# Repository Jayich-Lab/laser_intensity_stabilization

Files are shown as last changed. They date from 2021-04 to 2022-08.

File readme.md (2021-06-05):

# Laser Intensity Stabilization
<div align="center">
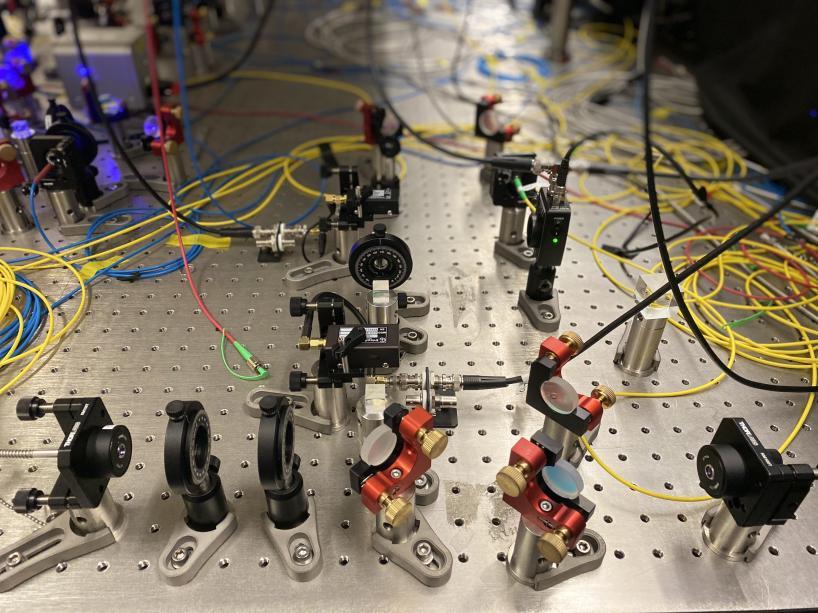
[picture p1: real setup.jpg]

</div>

[Development Notebook](https://docs.google.com/document/d/1RtXi4E6TiI_Ld4MZSRgFrHrQVlKGbRzDl3qZmrDYwTk/edit#)

We are aiming to stabilize intensity of laser to a fluctuation range of plus-minus 1% using Acousto-Optic Modulator (AOM) for a long timescale (in the order of days). This stabilization will improve the precision of experiments that use laser beams.

## Table of Contents
- [Motivation](#Motivation)
  - [P 3/2 Life Measurement](#P-32-Life-Measurement)
  - [Problems](#Problems)
  - [Goal](#Goal)
- [List of Components](#List-of-Components)
- [Schematics](#Schematics)
  - [Experiment Setup Schematics](#Experiment-Setup-Schematics)
  - [Acousto-Optics Modulator (AOM)](#Acousto-Optics-Modulator-AOM)
  - [Red Pitaya](#Red-Pitaya)
  - [Voltage Variable Attenuator (VVA)](#Voltag-Variable-Attenuator-VVA)
- [Feedback Loop](#Feedback-Loop)
  - [PID Controller](#PID-Controller)
  - [Code](#Code)
  - [Continuous (CW) Feedback](#Continuous-CW-Feedback)
  - [Pulsed Feedback](#Pulsed-Feedback)
- [Iterations](#Iterations)
  - [PI Stabilization](#PI-Stabilization)
  - [I Stabilization](#I-Stabilization)
- [Future Plans](#Future-Plans)
- [Contributors](#Contributors)

# Motivation
## P 3/2 Life Measurement
<div align="center">

</div>
We want to measure the lifetime of the P 3/2 lifetime of the radium-226 ion. For this measurement, we need to stabilize a detuned 802 nm laser which will be used for probing the  D 5/2 to P 3/2 transitions. The need for laser intensity stabilization comes from the concept of Rabi flopping. When we raise an ion from its ground state to an excited state, it doesn’t simply remain excited; rather, it oscillates back and forth from the ground state to the excited state at a frequency known as the Rabi frequency. The Rabi frequency is directly proportional to the laser intensity. If the laser intensity is not stable, then the excitation oscillation will shift. We will end up with ions between the excited and ground state, which will increase the systematic errors in our measurements. 

## Problems
Laser intensity drifts with time, and the amplitude drift could result in un-precise energy level transition, which affects energy shift induced by ac-stark shift of detuned laser. This unstable laser intensity affects the precision of Ra-226 excitation.

## Goal
Our goal for this research is to find a laser stabilization method that works for any lasers with any desired intensity. Users are able to manually set the desired intensity. The proportional and integral constants in the PID controller will be able to change on its own corresponding to the input signals.

# List of Components

- Photo Diode: [PDA10A2](https://www.thorlabs.com/thorproduct.cfm?partnumber=PDA10A2)
- Acousto Optic Modulator: [ATM-802DA1](https://intraaction.com/wp-content/themes/Divi/pdf/ATMModSeries08991.pdf)
- Laser: [SYNCROLASE-100](https://en.yuyiparts.com/aerotech-syncrolase-100-helium-neon-laser.html)
- Voltage Controlled Oscillator: [ZX95-100-S+](https://www.minicircuits.com/WebStore/dashboard.html?model=ZX95-100-S%2B)
- Voltage Variable Attenuator: [ZX73-2500-S+](https://www.minicircuits.com/WebStore/dashboard.html?model=ZX73-2500-S%2B)
- RF Amplifier: [ZHL-1-2W+](https://www.minicircuits.com/WebStore/dashboard.html?model=ZHL-1-2W%2B)

# Schematics
## Experiment Setup Schematics
<div align="center">
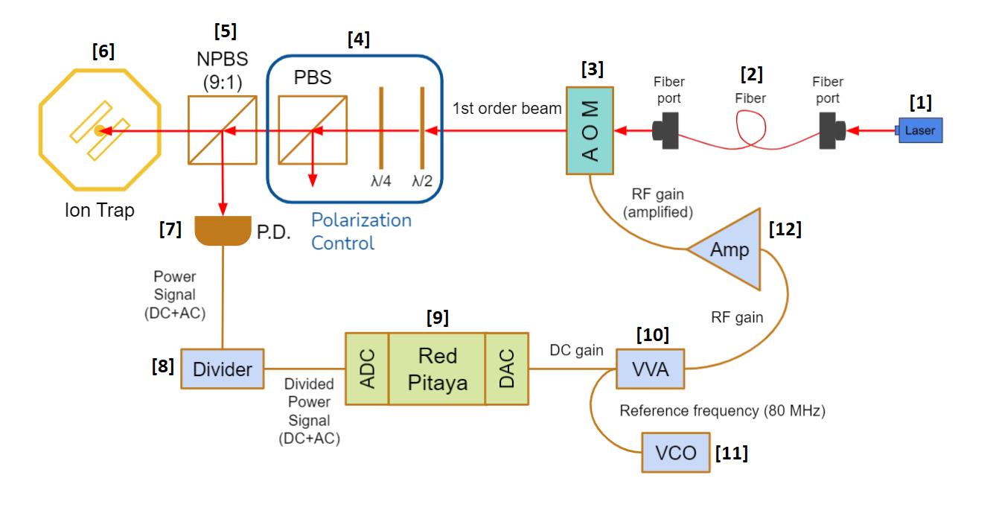
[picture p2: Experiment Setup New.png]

</div>

First, the laser beam [1] is transmitted by the fiber and goes through the two fiber ports [2]. It then is received by the [Acousto-Optic Modulator (AOM)](#Acousto-Optics-Modulator-AOM) [3], which diffracts the light to different intensity. We use the first order beam in our project. Next, the beam coming out from the AOM goes through the PBS (Polarizing Beam Splitter) [4] and the NPBS (Non-Polarizing Beam Splitter) [5]. These two beam splitters split the light and control the amount of light that goes into the ion trap [6] and the photodiode [7]. We choose an NPBS that splits 90 percent of the light and lets 10 percent of the power go into the photodiode. The photodiode is the detector of laser intensity in our project. It converts the light signal into voltage, which can then be received and analyzed by the PID program in Red Pitaya. The photodiode generates a voltage signal in the range of ± 4 volts and outputs it to the Red Pitaya. A ¼ divider [8] is put between the photodiode and the Red Pitaya to compensate the limitation that Red Pitaya can only take a voltage from -1 to 1 volt. A PID program is built in [Red Pitaya](#Red-Pitaya) [9]. It collects signals from the photodiode and compares it to a setpoint voltage to create an error signal. The Red Pitaya will then return this DC gain error signal and send it to a [voltage variable attenuator (VVA)](#Voltage-Variable-Attenuator-VVA) [10]. VVA receives this DC gain signal as well as an RF reference signal sent from the VCO (voltage control oscillator) [11], and it will output an attenuated RF gain with attenuation determined by the input control voltage (see the attenuation graph in the VVA section). The RF gain is then amplified by an RF amplifier [12] and sent back into the AOM to alter the intensity that goes through it.

## Acousto-Optics Modulator (AOM)
<div align="center">
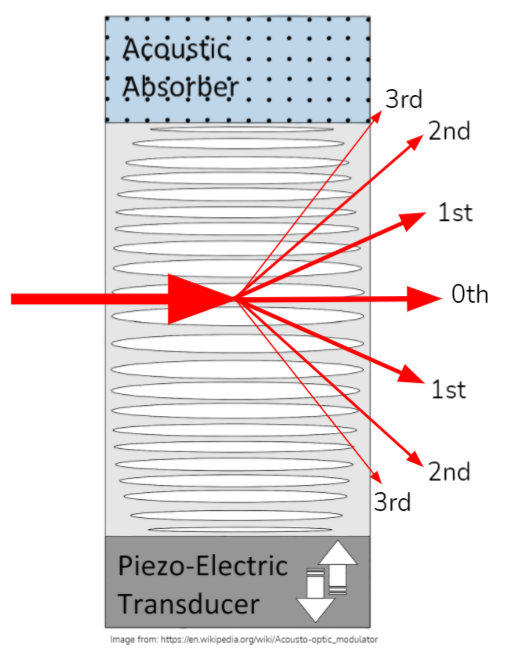
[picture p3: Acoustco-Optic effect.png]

</div>

An AOM uses the acousto-optic effect, which is similar to the Bragg diffraction, to diffract and shift the frequency of the incident light. The acousto-optic effect describes the diffraction of light by acoustic waves. The basis of this effect is a general effect of photoelasticity consisting in the change of the medium permittivity under the action of a mechanical strain. With the acousto-optic effect, the amount of light diffracted by the sound wave depends on the intensity of the sound. Thus, we use the intensity of the sound to modulate the intensity of the light.

For our project, we choose the first order beam from the AOM. The difference between each order beam is that they have different dynamic ranges. The dynamic range is the ratio between the largest and smallest values of the intensity that can be outputted by the AOM. For the zeroth order beam, the intensity can be attenuated from 100 percent to 20 percent, which provides a dynamic range from 100 to 300; while for the first order beam, the intensity can be attenuated from 85 percent to 0 percent, which provides a dynamic range from 100 all the way to infinity. Thus, we choose the first order beam for our project to have a larger dynamic range.

The intensity of the first order beam is controlled by the control signal that goes into the AOM. When the control signal increases, the intensity increases correspondingly. We adjust the intensity of the laser using this property of the AOM.

## Red Pitaya
<div align="center">
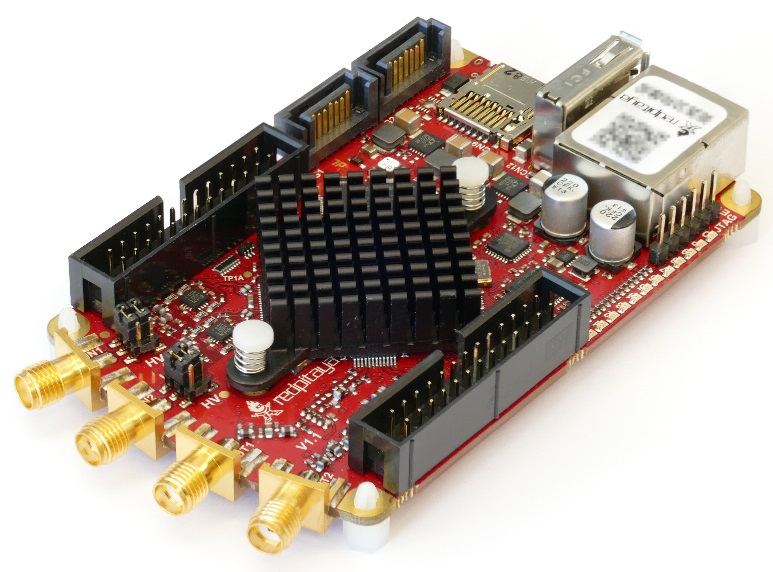
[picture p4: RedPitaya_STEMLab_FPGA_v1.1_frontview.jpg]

</div>

Red Pitaya is an affordable, PC based, multi instrument. It acts as the brain of our project, which takes up the role of PID controller for the feedback loop (Discussed in Feedback Loop Section). Signal coming from the photodiode is received by the DAC portal of the Red Pitaya, and after the PID program an output signal will be sent out from the ADC portal to the voltage variable attenuator (VVA).

## Voltage Variable Attenuator (VVA)
<div align="center">
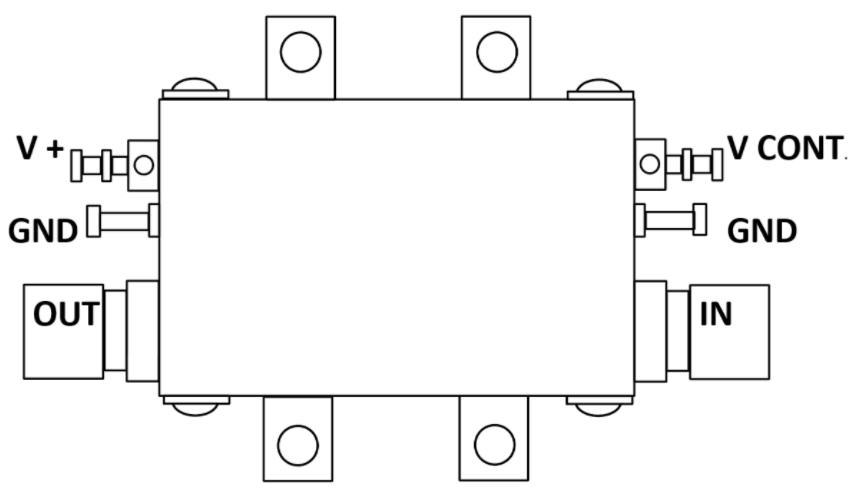
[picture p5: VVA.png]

</div>

Attenuators are transmission line components used to reduce the input power in a system by a predetermined amount. It is operated throughout its entire dynamic range. Different from fixed attenuators, variable attenuators can be controlled to vary the attenuation level of the device with a number of different methods. A voltage variable attenuator, the VVA, has its attenuation controlled by the voltage. The typical attenuation of the VVA we use, ZX73-2500+ attenuator, is shown in the figure below.
<br>
<div align="center">

</div>

From the figure above, we can see that the attenuation of our ZX73-2500+ attenuator is non-linear, with the curve relatively linear and flat at control voltage range 0 to 0.5 volts and at high voltage. These linear regions imply that at these two control voltage ranges, the attenuation of the VVA does not change dramatically under large control voltage change. This property of the VVA helps to diminish the overcompensation of the PID program and prevent it from destroying the whole feedback loop. An overcompensation of the PID program means that the PID overcompensates for every positive error and creates an even larger error in the negative direction (and vice-versa). With a VVA in the circuit, the overcompensation from the PID feedback can be diminished and it will not cause serious failure in the stabilization. To achieve high precision, we require the input control signal at higher voltage. We choose 4-12 volts as our range of control voltage in our project.

# Feedback Loop
## PID Controller
<div align="center">

</div>

Red Pitaya is remotely controlled using a client on a computer via an internal network. After receiving the signal, the pitaya runs a python script (discussed in [Code](#Code)) section, compares the input voltage to the setpoint voltage, and applies a control signal, C, which depends on the proportional, integral and differential terms of the error signal. The relationship can be seen in the equation above. We neglected the differential term for our setup as we weren’t concerned with stabilizing at high frequency (laser fluctuations tended to be low frequency). The control signal from the pitaya goes through an operational amplifier which increases the control range from ± 1 volt to 4 and 12 volts. The [Voltage Variable Attenuator (VVA)](#Voltage-Variable-Attenuator-VVA) section explains why we want to be in the 4 -12 voltage range. The control signal was also sent to an oscilloscope at the same time. The majority of the data was taken on an oscilloscope. The data from the oscilloscope was read by a server on the computer and sent to the red pitaya. The computer (server and client) are constantly communicating with the red pitaya during  the feedback loop. 

## Code
The programming was mainly done on the red pitaya using python and the PyRPL module, which has python defined classes for controlling the pitaya outputs and inputs. The PyRPL code was written onto a server, and a client was then made using that server. 
There was also a simpler script made for an independent laser intensity stabilization setup using an Arduino due. The code is above under “PI_Stabilization.ino”. The Arduino presents versatility as it uses C++, a widely accessible programming language. On the other hand, the red pitaya can either be programmed using the limited PYRPL module or the native language of the pitaya, Verilog, which is less accessible. 
Either the Arduino or the pitaya is sufficient for stabilization. Still, when it comes to pulsed feedback (discussed shortly), the Arduino is a better choice as C++ is easier to work with than Verilog. 

## Continuous (CW) Feedback
<div align="center">
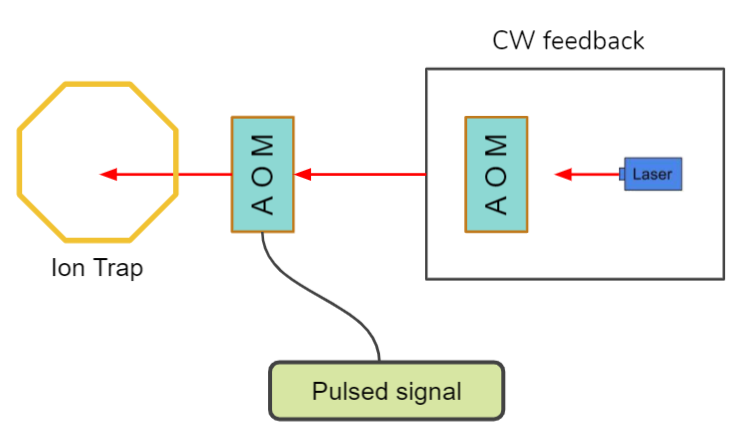
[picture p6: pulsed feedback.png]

</div>

We need to identify a clear distinction between continuous and pulsed feedback. In this experiment, we are applying continuous waveform (CW) feedback. We are continuously reading data and stabilizing it over time. The picture above illustrates a summary of our CW feedback in a rectangle on the right. Generally, in ion trap experiments, laser beams are sent to the ion trap in pulse sequences (on the order of microseconds). We can create a stabilized pulsing laser by placing a second AOM after the laser is stabilized. The second AOM will receive a signal that turns it “on” or “off,” This way, we have a pseudo pulsed feedback setup. 

## Pulsed Feedback
<div align="center">

</div>
We created pseudo pulsed feedback, but what does pulsed feedback look like? Unlike CW feedback, in pulsed feedback, we only take data on short intervals (µs). The above graph models a pulse sequence where the laser is on for µs and off for ms. During the period the laser is on, a microcontroller collects data and generates an error signal E1. When the laser is off, the microcontroller outputs a constant dc offset. After the laser is turned on again, a fixed dc voltage (red line) is outputted based on the error signal E1. This process continues for all pulses.
<br>
*Note only CW feedback was used in this project 

# Iterations
## PI Stabilization
<div align="center">

</div>
<br>

Laser intensity was stabilized to ± 0.2%, which surpasses our goal of ± 1%. The blue plot is the signal received by the photodiode, the orange curve is the control signal output by the red pitaya, and the green line is the stabilized signal.  We took the data in 8 hours and found no drifts in the stabilization, which indicates that our setup is robust since it maintains the same intensity while environmental parameters such as temperature change. Using only the P and I terms, we were able to minimize the initial noise by a factor of 200. 
<br><br>

<div align="center">
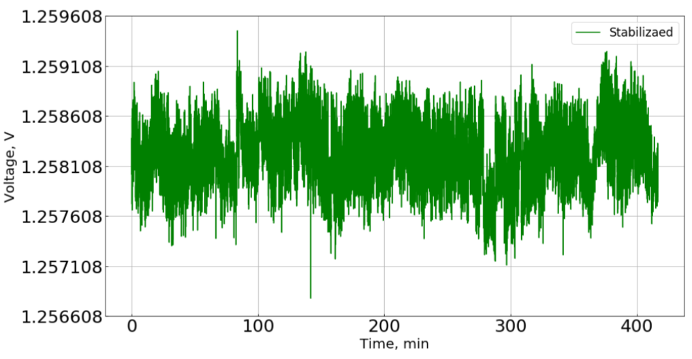
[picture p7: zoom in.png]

</div>
<br>

Looking more closely at the stabilized signal, we can see no long-term drift; the signal only oscillates at high frequency. This high-frequency noise can be accounted for by the internal noise of the photodiode. The ± 0.2% fluctuation in our data was partly correlated to the photodiode uncertainty; the rest of the noise comes from the control signal output by the pitaya. The above data set was preliminary data and demonstrated the sufficiency of our stabilization for the P 3/2 life measurement. 

## I Stabilization
<div align="center">
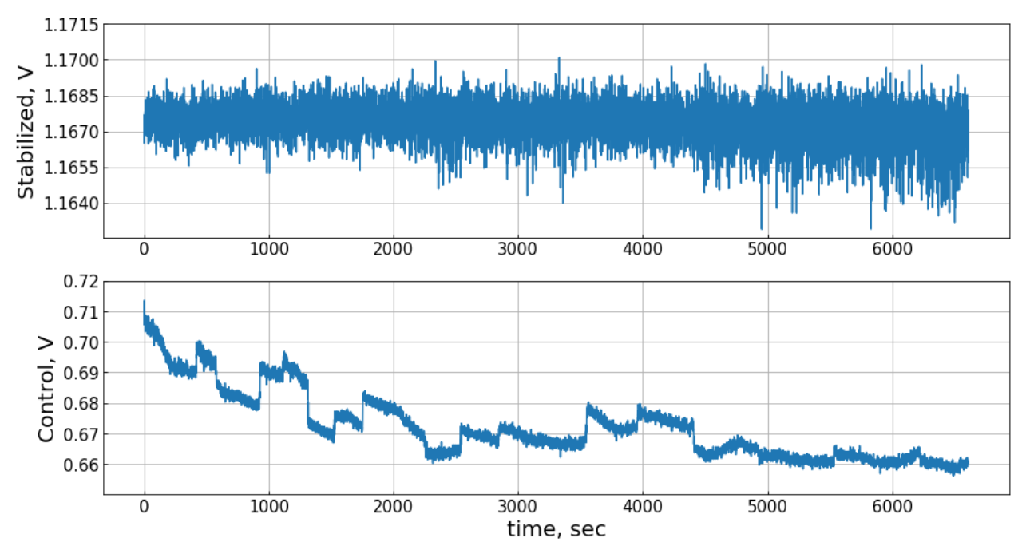
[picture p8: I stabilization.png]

</div>

Using 802 nm laser light (20% intensity fluctuation without stablilization), we stablilized the laser to average within ± 0.1% of our setpoint intensity. Extreme peaks during stablization still stayed within ± 0.3% of setpoint.  Long term drift of intensity from 802 nm is no longer a problem with this intensity stabilizer. The graph above was taken  on the laser that was used for the P 3/2 life time measurement. 

Observations:
1. It was found that **omitting** the proportional term for PID control was more stable than including proportional control.
2. The lower the control voltage (shown in the bottom graph as it slopes downward), the less stablity we get due to the VVA response curve at different voltages.

# Future Plans
<div align="center">
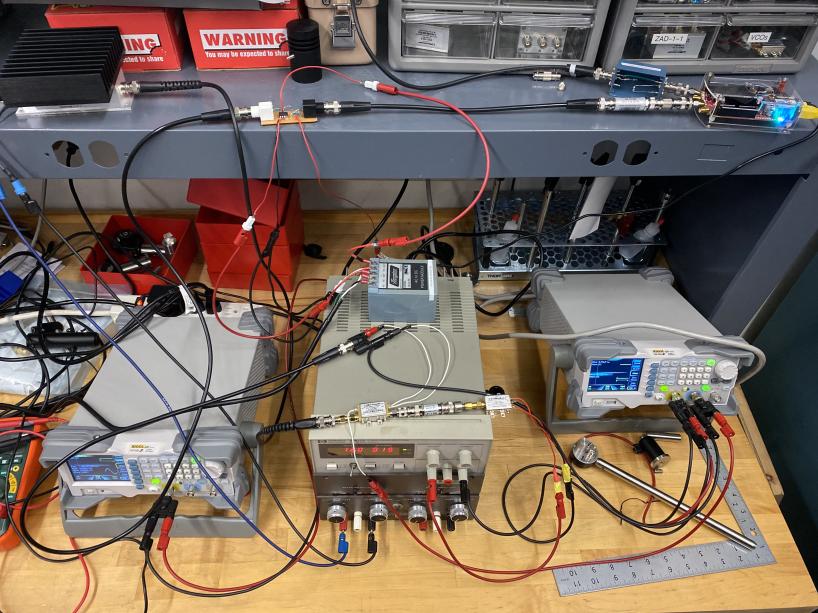
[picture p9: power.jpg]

</div>
<br>

There are some issues with our current pseudo pulsed feedback setup. 1) We can’t stabilize the laser intensity right before the beam reaches the ion trap; it has to go through different optics before reaching the trap, which means it will incur some extra noise that we can’t currently stabilize. 2) The second AOM (the one receiving pulsed signal) changes how fast it can turn on and off based on the environmental temperature. 3) Our current setup, as you can see from the picture above, uses too many separate power supplies, which makes it difficult to set up and apply to any measurement. 
Potential solution: utilize an [Arduino DUE](https://store.arduino.cc/usa/due) to make independent pulsed feedback. This would eliminate the second AOM and allow us to stabilize the laser light right before it reaches the ion trap.We would also be able to make an integrated power supply, making our stabilization more compact and robust. 

# Contributors
This project is made for CS 15C class by Chaoshen Zhang, Sam Gebretsadkan, Vivian Liao and Rei Landsberger.

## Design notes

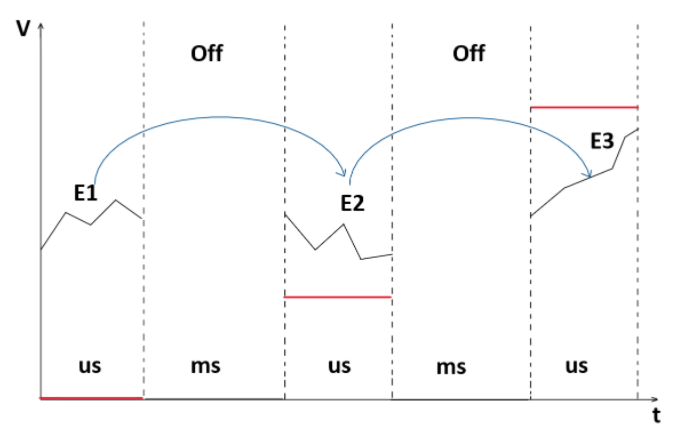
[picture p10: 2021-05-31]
pulsed feedback fig.png

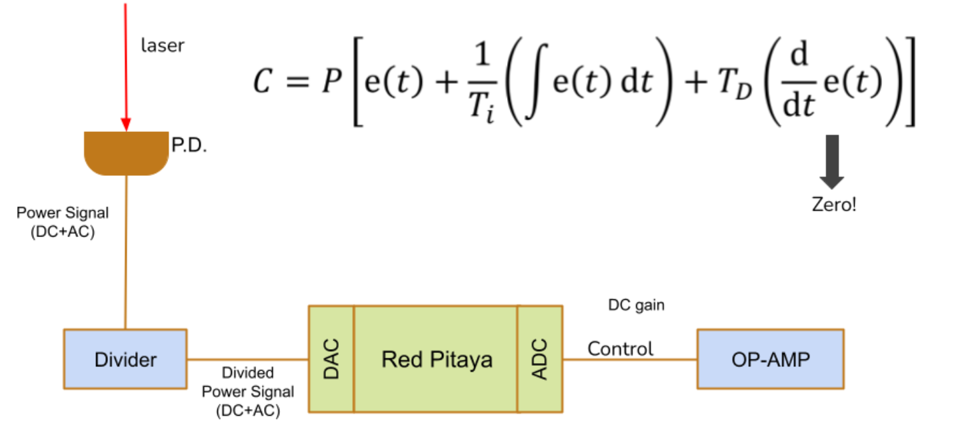
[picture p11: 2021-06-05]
PID controller.png

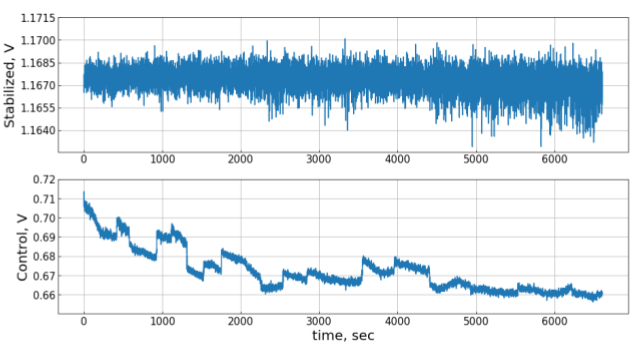
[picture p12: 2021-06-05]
802nm_stabilization.png

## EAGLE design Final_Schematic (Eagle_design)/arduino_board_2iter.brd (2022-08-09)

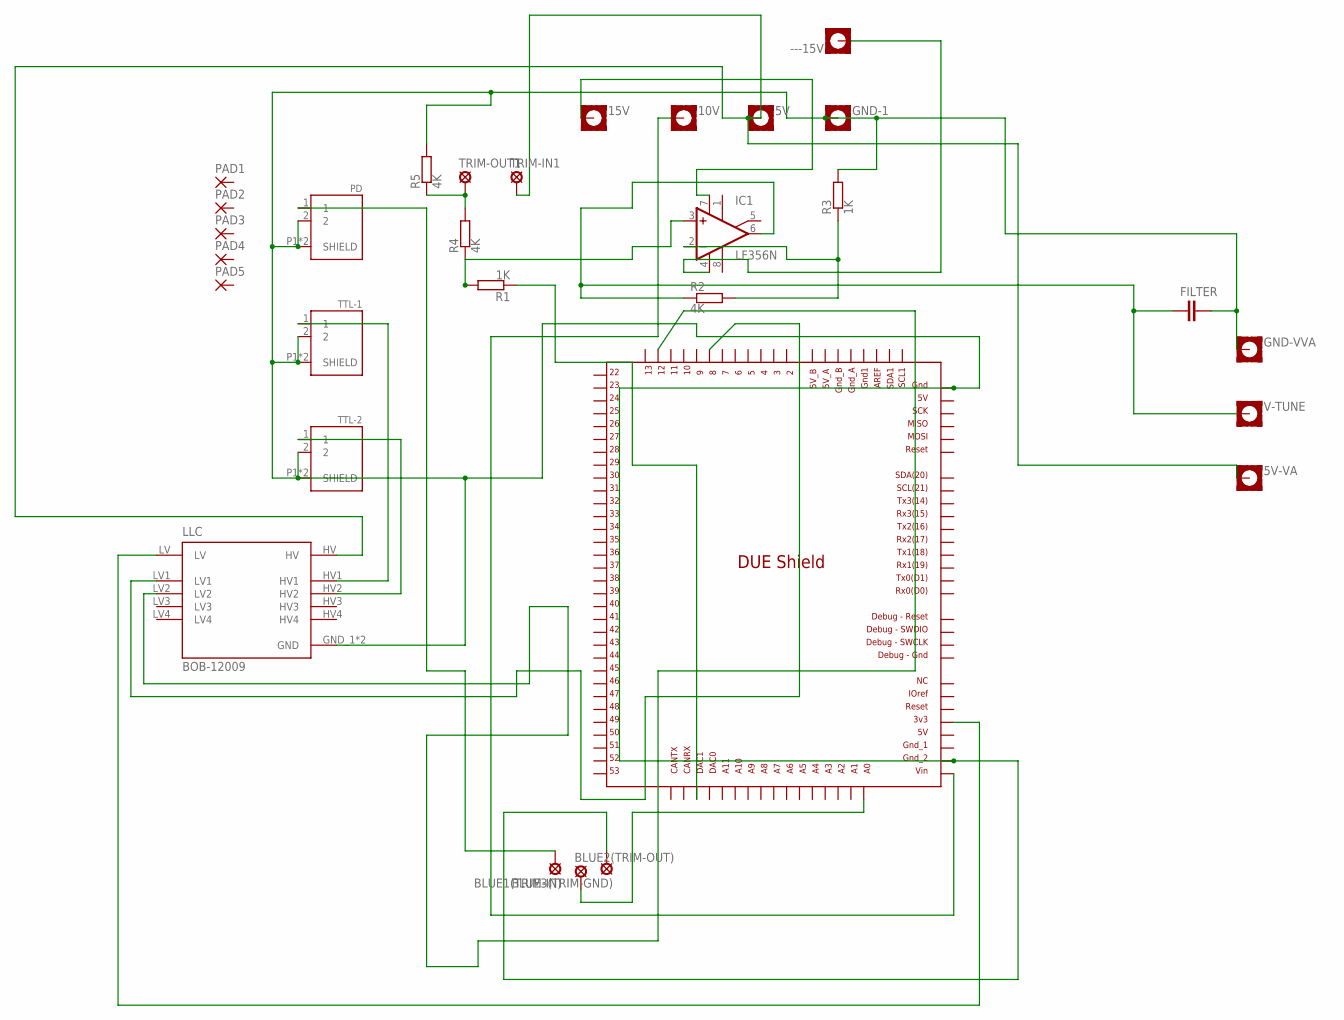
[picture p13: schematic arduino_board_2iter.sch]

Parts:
5V, 5V-VA, 10V, 15V: MOUNT-PAD-SQUARE2.8; 2,8-PAD-SQUARE
---15V: MOUNT-PAD-SQUARE2.8; 2,8-PAD-SQUARE
BLUE1(TRIM-IN), BLUE2(TRIM-OUT), BLUE3(TRIM-GND): LSP10
FILTER: C-EUC1812K; C1812K
GND-1: MOUNT-PAD-SQUARE2.8; 2,8-PAD-SQUARE
GND-VVA: MOUNT-PAD-SQUARE2.8; 2,8-PAD-SQUARE
IC1: LF356N; DIL08
LLC: BOB-12009; CONV_BOB-12009
PAD1, PAD2, PAD3, PAD4, PAD5: 1,6/0,9
PD: 1-1337543-0; CONN_1-1337543-0
R1, R3: 1K; SMS-0
R2, R4, R5: 4K; SMS-0
TRIM-IN1: LSP10
TRIM-OUT1: LSP10
TTL-1, TTL-2: 1-1337543-0; CONN_1-1337543-0
U$1: DUE(NORMAL)
V-TUNE: MOUNT-PAD-SQUARE2.8; 2,8-PAD-SQUARE

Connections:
GND: BLUE3(TRIM-GND).MP, FILTER.2, GND-1.B2,8, GND-VVA.B2,8, LLC.GND_1 (GND), LLC.GND_2 (GND), PD.2, PD.P1 (SHIELD), PD.P2 (SHIELD), R3.1, R5.1, TTL-1.2, TTL-1.P1 (SHIELD), TTL-1.P2 (SHIELD), TTL-2.2, TTL-2.P1 (SHIELD), TTL-2.P2 (SHIELD), U$1.5V_ICSP, U$1.GND_2
unnamed: IC1.3 (+IN), R1.1, R4.2
unnamed: FILTER.1, IC1.6 (OUT), R2.2, V-TUNE.B2,8
unnamed: IC1.2 (-IN), R2.1, R3.2
unnamed: 10V.B2,8, U$1.VIN
unnamed: R1.2, U$1.DAC1
unnamed: 15V.B2,8, IC1.7 (V+)
unnamed: LLC.LV, U$1.3V3
unnamed: LLC.HV1, TTL-1.1
unnamed: LLC.HV2, TTL-2.1
unnamed: BLUE1(TRIM-IN).MP, PD.1
unnamed: 5V.B2,8, 5V-VA.B2,8, LLC.HV, TRIM-IN1.MP
unnamed: LLC.LV2, U$1.12
unnamed: BLUE2(TRIM-OUT).MP, U$1.A0
unnamed: R4.1, R5.2, TRIM-OUT1.MP
unnamed: ---15V.B2,8, IC1.4 (V-)
unnamed: LLC.LV1, U$1.8

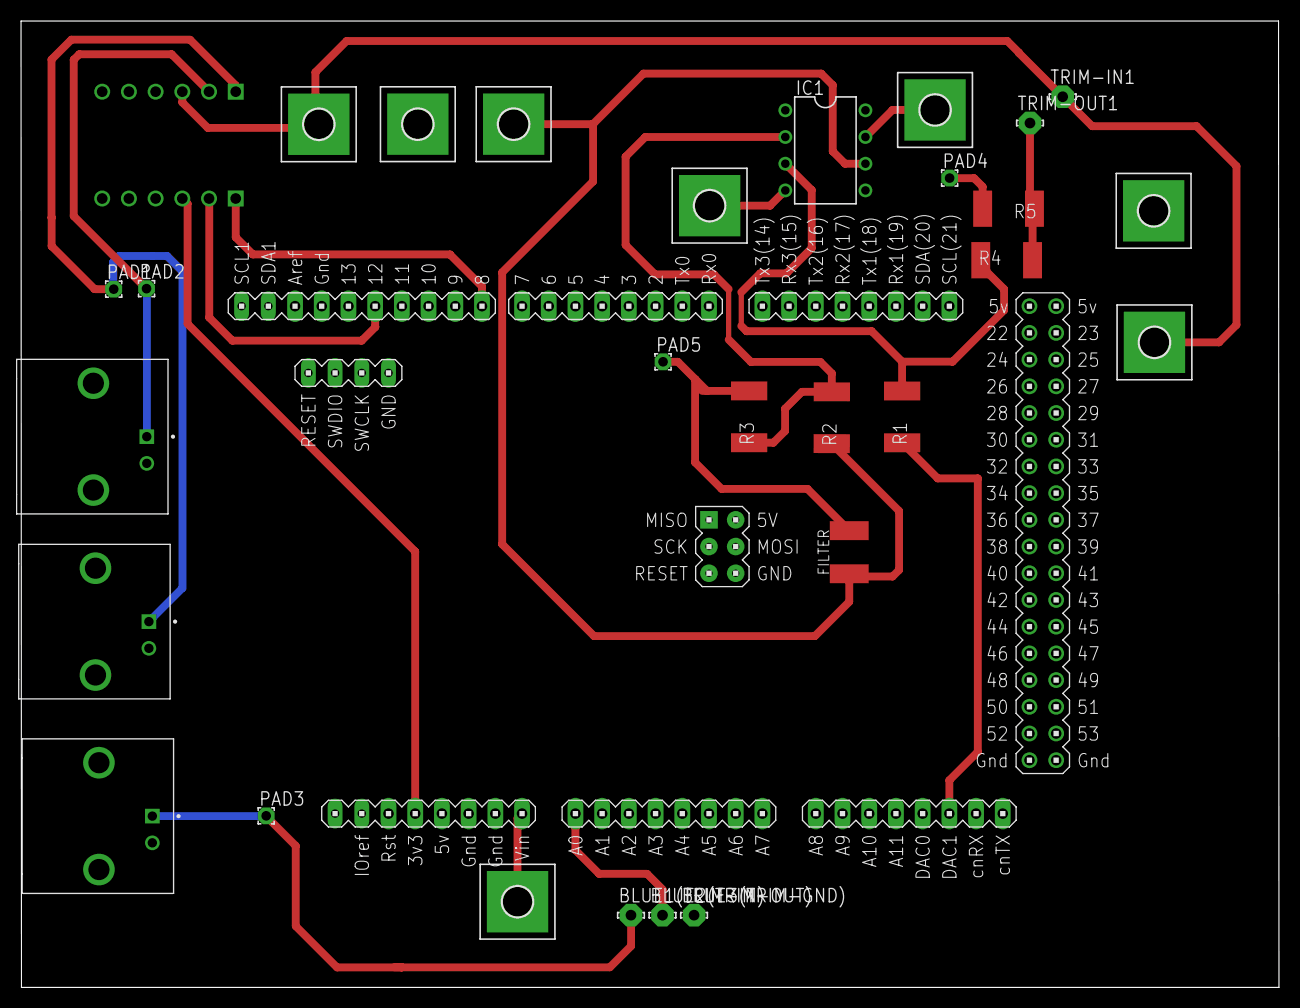
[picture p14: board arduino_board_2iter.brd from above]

Board: 2 copper layers, 119.6 x 91.9 mm, 30 parts (1 on the bottom side), 17 nets.

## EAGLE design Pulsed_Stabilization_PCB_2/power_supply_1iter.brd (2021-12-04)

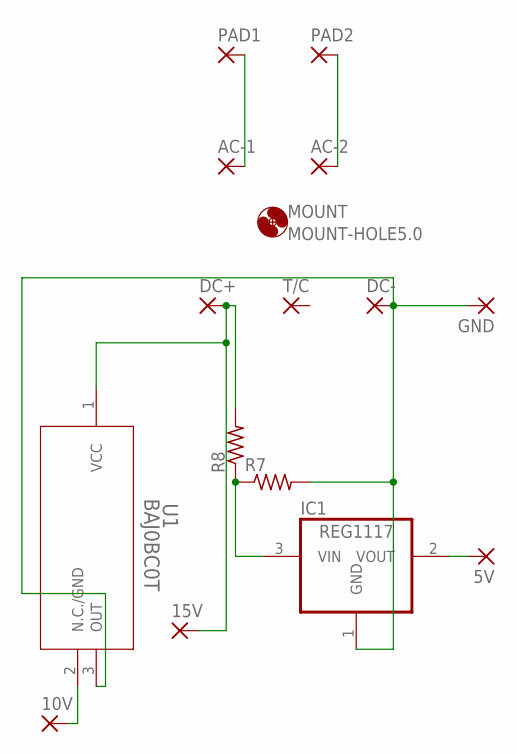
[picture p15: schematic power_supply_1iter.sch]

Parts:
5V, 10V, 15V: 3,17/1,1
AC-1, AC-2: 3,81/1,1
DC+: 3,81/1,1
DC-: 3,81/1,1
GND: 3,17/1,1
IC1: REG1117; SOT223_HEATSINK
MOUNT: MOUNT-HOLE5.0; 5,0
PAD1, PAD2: WIREPAD4,16O1,6; 4,16O1,6
R7, R8: R-US_0309/12; 0309/12
T/C: 3,81/1,1
U1: BAJ0BC0T; TO220FP-3_ROM

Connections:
unnamed: AC-1.1, PAD1.1
unnamed: AC-2.1, PAD2.1
unnamed: 15V.1, DC+.1, R8.2, U1.1 (VCC)
unnamed: DC-.1, GND.1, IC1.1 (GND), R7.2, U1.3 (OUT)
unnamed: IC1.3 (VIN), R7.1, R8.1
unnamed: 10V.1, U1.2 (N.C./GND)
unnamed: 5V.1, IC1.2 (VOUT)

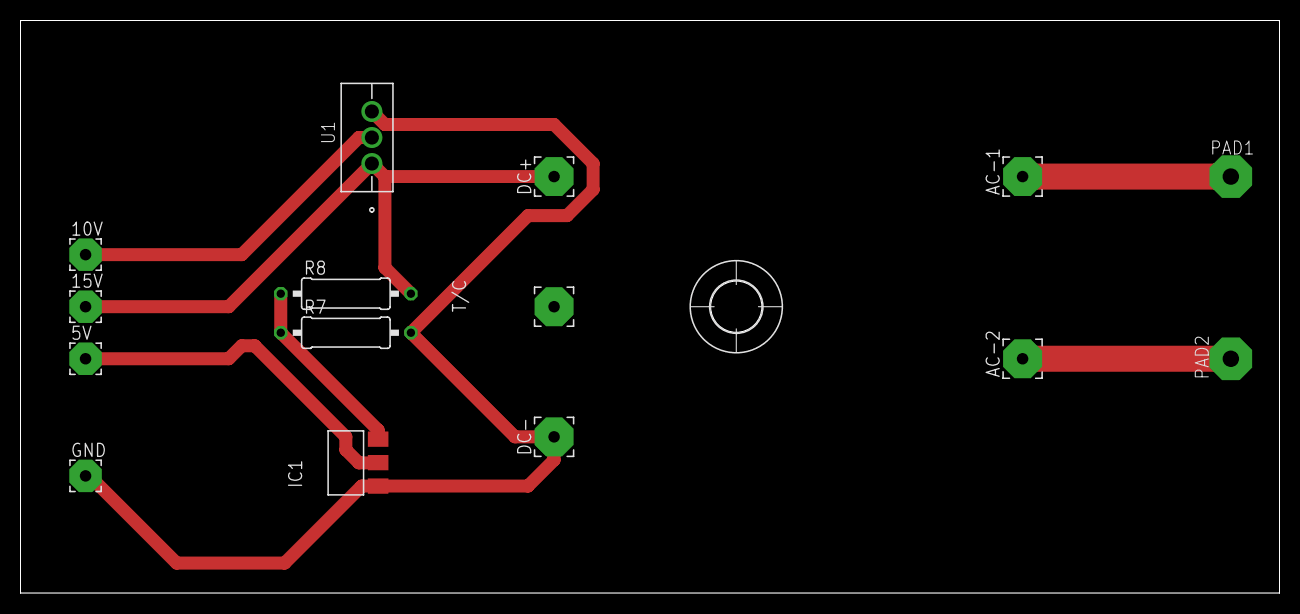
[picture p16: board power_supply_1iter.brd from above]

Board: 2 copper layers, 122.9 x 55.9 mm, 16 parts (0 on the bottom side), 7 nets.

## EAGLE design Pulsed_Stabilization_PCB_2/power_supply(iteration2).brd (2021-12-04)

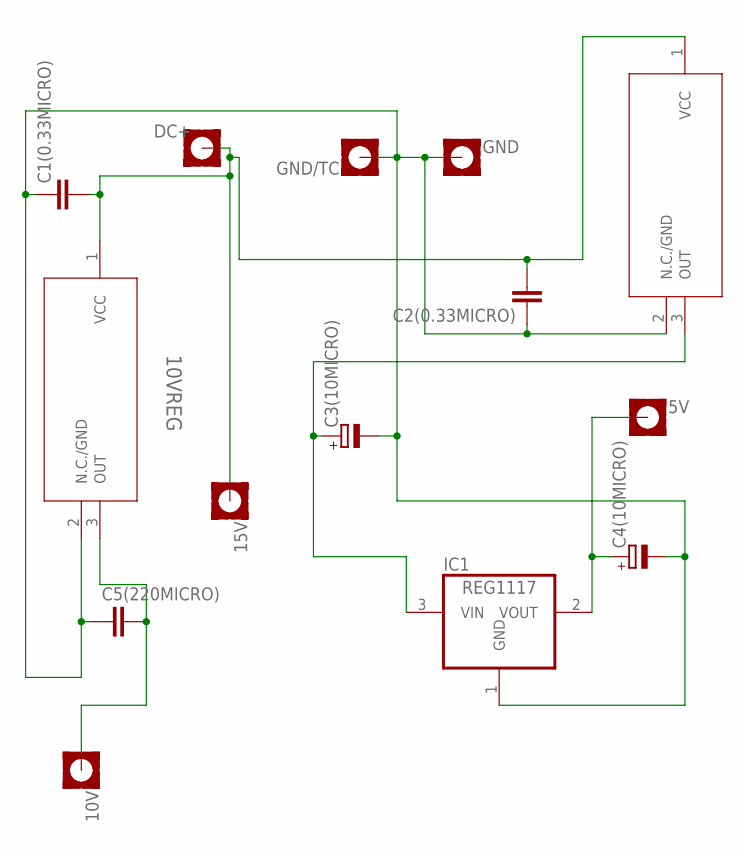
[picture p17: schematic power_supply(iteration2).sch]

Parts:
5V, 10V, 15V: MOUNT-PAD-SQUARE2.8; 2,8-PAD-SQUARE
10VREG, 10VREG1: BAJ0BC0T; TO220FP-3_ROM
C1(0.33MICRO), C2(0.33MICRO): C-EU025-025X050; C025-025X050
C3(10MICRO), C4(10MICRO): CPOL-EUE2.5-6; E2,5-6
C5(220MICRO): C-EUC1812K; C1812K
DC+: MOUNT-PAD-SQUARE2.8; 2,8-PAD-SQUARE
GND: MOUNT-PAD-SQUARE2.8; 2,8-PAD-SQUARE
GND/TC: MOUNT-PAD-SQUARE2.8; 2,8-PAD-SQUARE
IC1: REG1117; SOT223_HEATSINK

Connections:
unnamed: 10VREG.1 (VCC), 10VREG1.1 (VCC), 15V.B2,8, C1(0.33MICRO).2, C2(0.33MICRO).2, DC+.B2,8
unnamed: 10VREG.2 (N.C./GND), 10VREG1.2 (N.C./GND), C1(0.33MICRO).1, C2(0.33MICRO).1, C3(10MICRO).-, C4(10MICRO).-, C5(220MICRO).1, GND.B2,8, GND/TC.B2,8, IC1.1 (GND)
unnamed: 10V.B2,8, 10VREG.3 (OUT), C5(220MICRO).2
unnamed: 10VREG1.3 (OUT), C3(10MICRO).+, IC1.3 (VIN)
unnamed: 5V.B2,8, C4(10MICRO).+, IC1.2 (VOUT)

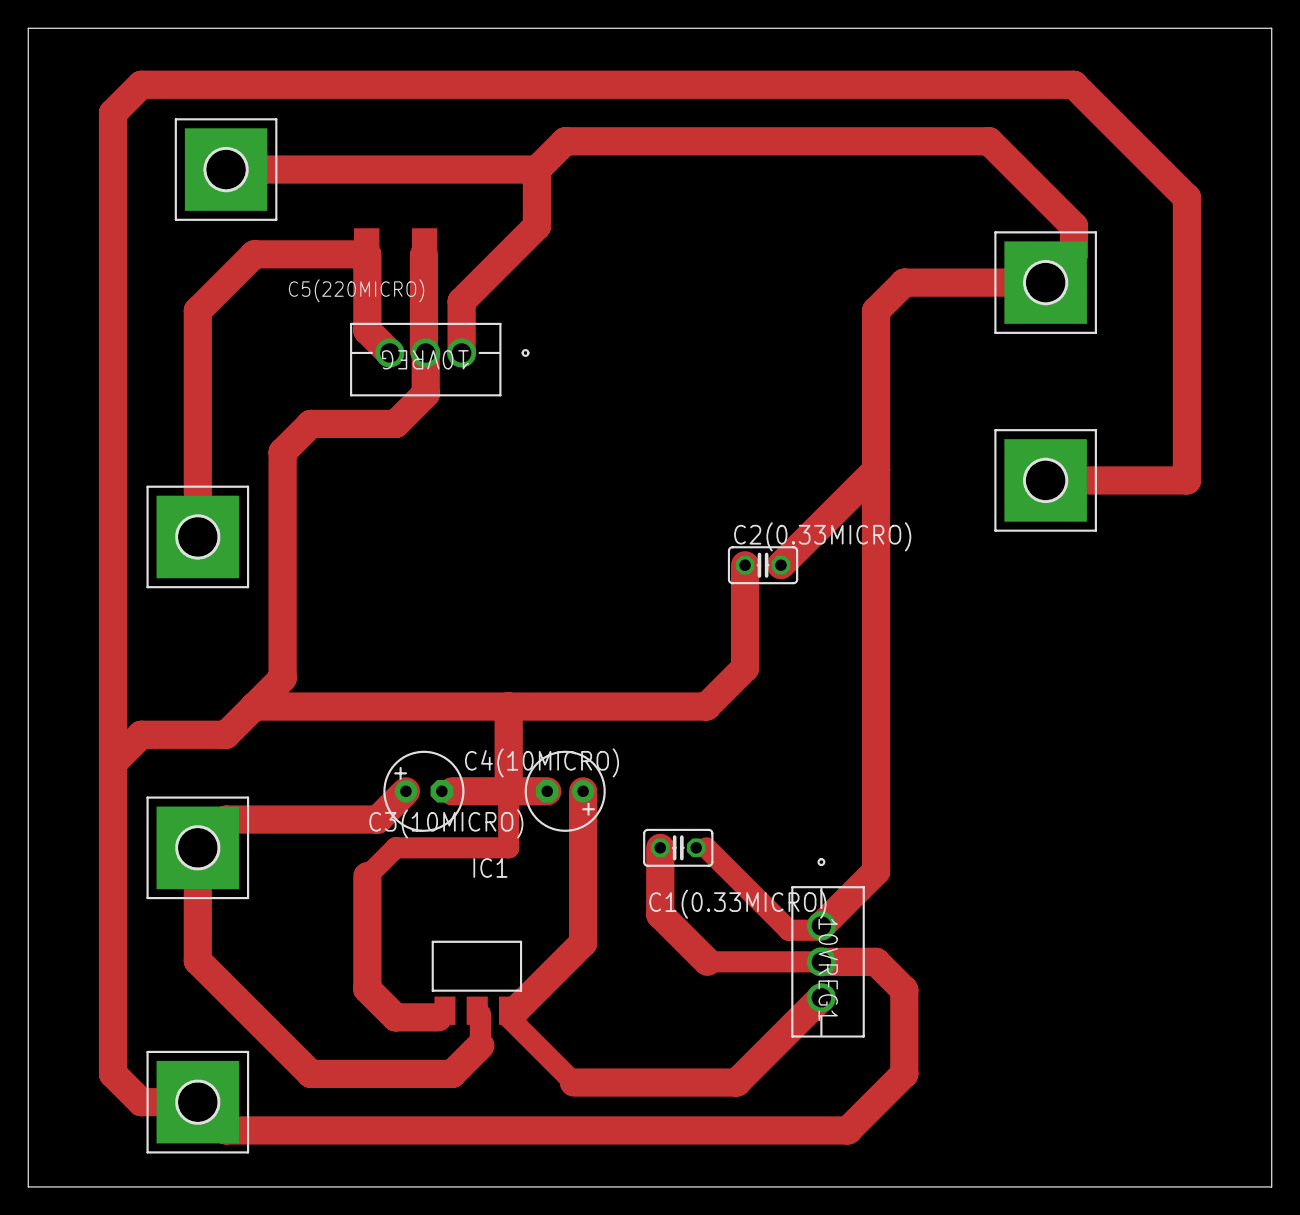
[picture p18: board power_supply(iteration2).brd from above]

Board: 2 copper layers, 88.0 x 82.0 mm, 14 parts (0 on the bottom side), 5 nets.

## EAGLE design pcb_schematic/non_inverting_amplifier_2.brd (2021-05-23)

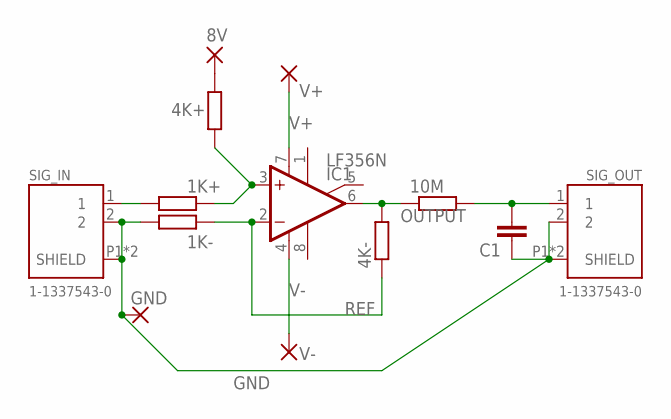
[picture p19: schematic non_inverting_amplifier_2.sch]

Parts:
1K+, 1K-, 4K+, 4K-, 10M: R-EU_0207/12; 0207/12
8V: 2,54/1,1
C1: C2,5-3; C2.5-3
GND: 2,54/1,1
IC1: LF356N; DIL08
SIG_IN: 1-1337543-0; CONN_1-1337543-0
SIG_OUT: 1-1337543-0; CONN_1-1337543-0
V+: 2,54/1,1
V-: 2,54/1,1

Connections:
GND: 1K-.1, C1.1, GND.1, SIG_IN.2, SIG_IN.P1 (SHIELD), SIG_IN.P2 (SHIELD), SIG_OUT.2, SIG_OUT.P1 (SHIELD), SIG_OUT.P2 (SHIELD)
unnamed: 1K+.1, SIG_IN.1
unnamed: 1K+.2, 4K+.1, IC1.3 (+IN)
unnamed: 4K+.2, 8V.1
unnamed: 10M.2, C1.2, SIG_OUT.1
OUTPUT: 4K-.2, 10M.1, IC1.6 (OUT)
REF: 1K-.2, 4K-.1, IC1.2 (-IN)
V+: IC1.7 (V+), V+.1
V-: IC1.4 (V-), V-.1

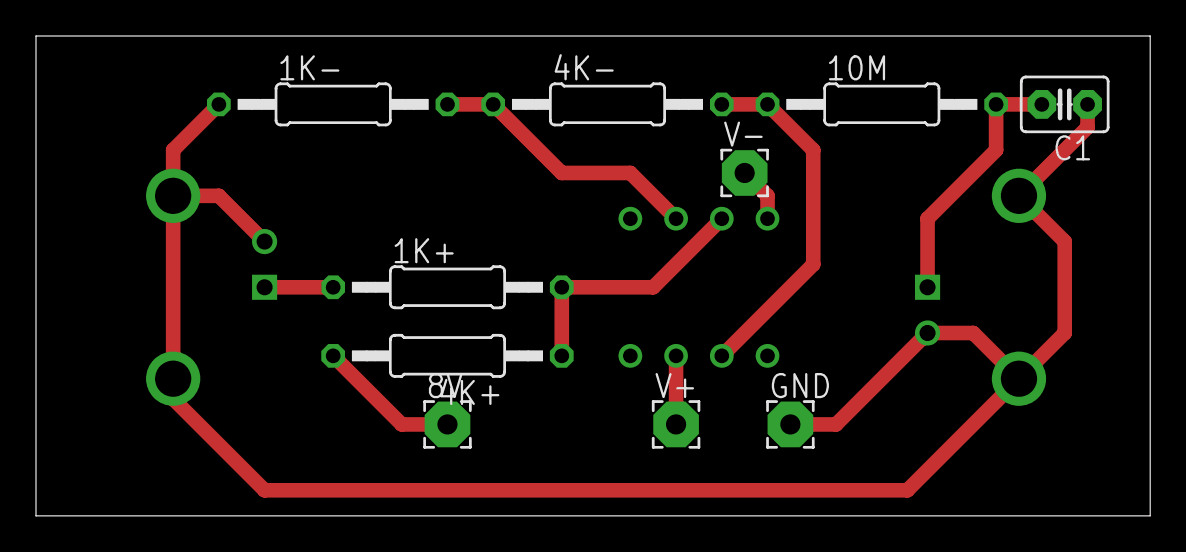
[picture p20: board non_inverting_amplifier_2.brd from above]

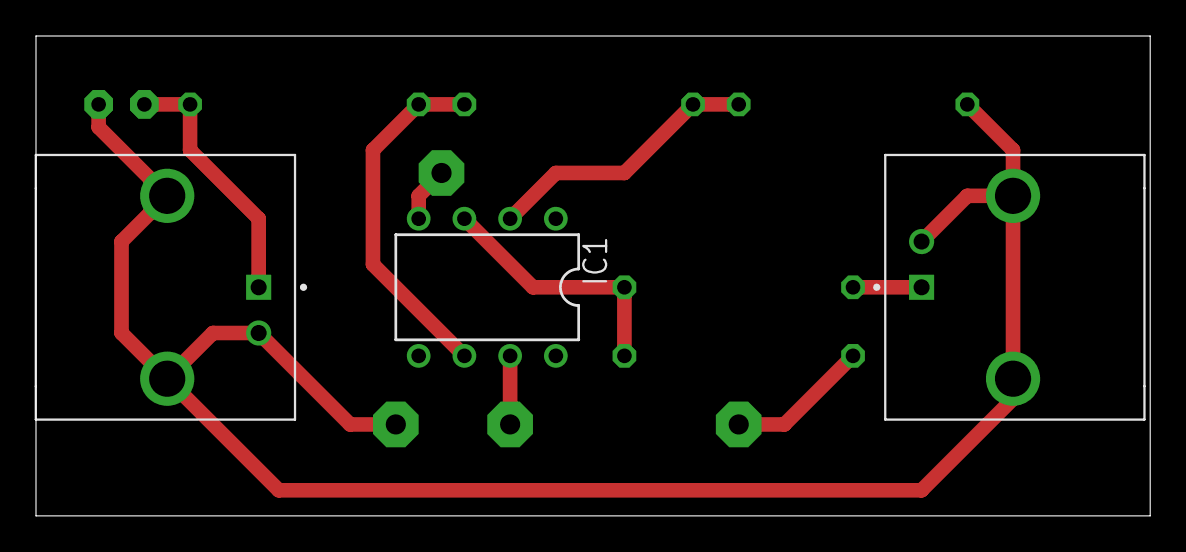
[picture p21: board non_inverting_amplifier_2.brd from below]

Board: 2 copper layers, 61.9 x 26.7 mm, 13 parts (3 on the bottom side), 9 nets.

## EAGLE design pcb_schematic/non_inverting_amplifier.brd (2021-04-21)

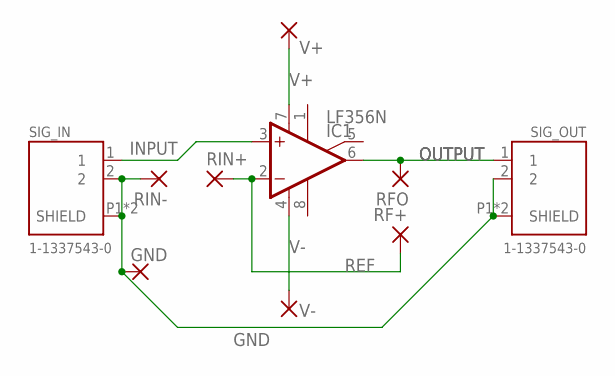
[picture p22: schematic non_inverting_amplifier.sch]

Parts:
GND: 2,54/1,1
IC1: LF356N; DIL08
RF+: 2,54/1,1
RFO: 2,54/1,1
RIN+: 2,54/1,1
RIN-: 2,54/1,1
SIG_IN: 1-1337543-0; CONN_1-1337543-0
SIG_OUT: 1-1337543-0; CONN_1-1337543-0
V+: 2,54/1,1
V-: 2,54/1,1

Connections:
GND: GND.1, RIN-.1, SIG_IN.2, SIG_IN.P1 (SHIELD), SIG_IN.P2 (SHIELD), SIG_OUT.2, SIG_OUT.P1 (SHIELD), SIG_OUT.P2 (SHIELD)
INPUT: IC1.3 (+IN), SIG_IN.1
OUTPUT: IC1.6 (OUT), RFO.1, SIG_OUT.1
REF: IC1.2 (-IN), RF+.1, RIN+.1
V+: IC1.7 (V+), V+.1
V-: IC1.4 (V-), V-.1

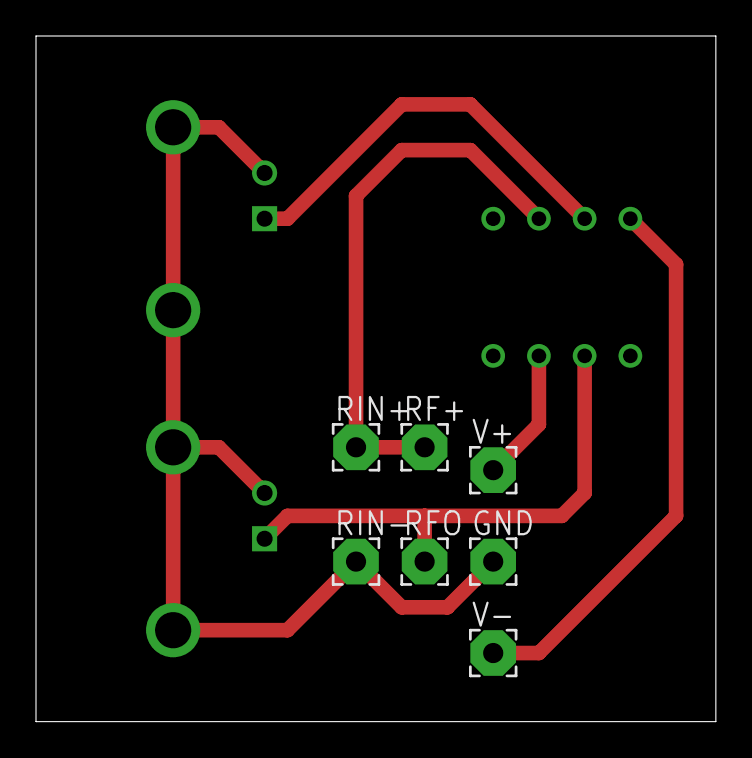
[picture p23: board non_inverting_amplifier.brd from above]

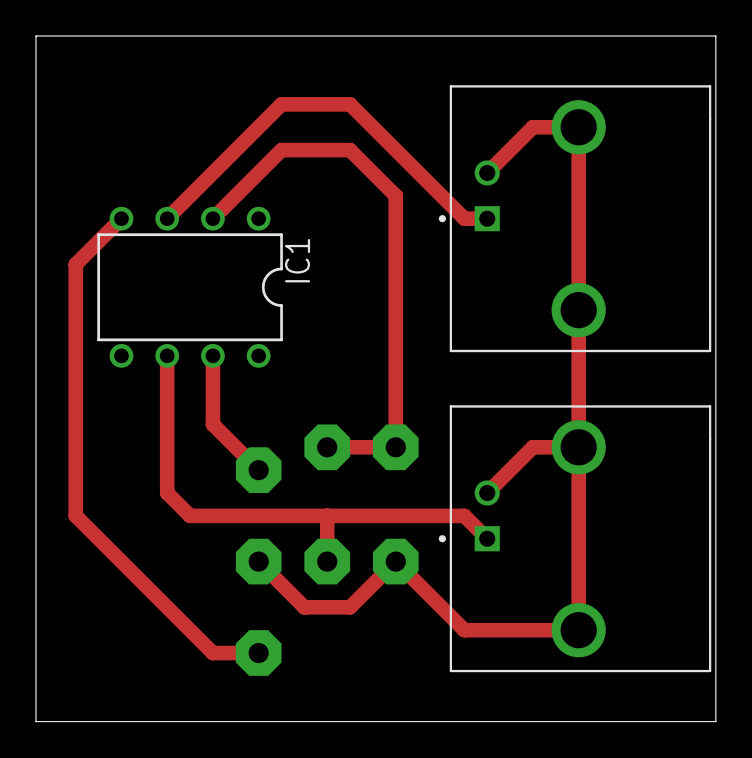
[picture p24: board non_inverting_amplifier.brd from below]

Board: 2 copper layers, 37.8 x 38.1 mm, 10 parts (3 on the bottom side), 6 nets.

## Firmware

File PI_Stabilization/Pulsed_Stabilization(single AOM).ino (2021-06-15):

int input_setpoint = 2047;
int output_setpoint = 2047;
float p_gain = 1.;
float i_gain = 0.;
float i_term = 0;
int error_range = 30;
int error[list_range];
int DIGITALPIN = 1;

void setup() {
  Serial.begin(115200);
  pinMode(DIGITALPIN, INPUT);
  ADC->ADC_MR |= 0x80; // these lines set free running mode on adc 7 (pin A0)
  ADC->ADC_CR = 2;
  ADC->ADC_CHER = 0x80;

  analogWriteResolution(12);
  analogWrite(DAC0, output_setpoint);
}

int read_adc() {
  while ((ADC->ADC_ISR & 0x80) == 0); // wait for conversion
  int a0 = ADC->ADC_CDR[7];            // read data
  return a0;
}

int push(int list, int range){
  for (int i=0, i<=range-2, i++){
    list[i] = list[i+1];
  }
  list[range-1] = read_adc()-input_setpoint;
  return list
}

float average (int * array, int range)  // assuming array is int.
{
  long sum = 0L ;  // sum will be larger than an item, long for safety.
  for (int i = 0 ; i < range ; i++)
    sum += array [i] ;
  return  ((float) sum) / range ;  // average will be fractional, so float may be appropriate.
}

void loop() {
  if (digitalRead == HIGH) {
    while (digitalRead == HIGH) {
      error = push(error, error_range);
    }
    if (digitalRead == LOW) {
      int correction = (int)(average(error, error_range));
      output_setpoint += correction;
      analogWrite(DAC0, output_setpoint);
    }
  }
}

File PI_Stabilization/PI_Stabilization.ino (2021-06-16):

int input_setpoint = 2047;
int output_setpoint = 2047;
float p_gain = 1.;
float i_gain = 0.;
float i_term = 0;

void setup() {
  Serial.begin(115200);

  ADC->ADC_MR |= 0x80; // these lines set free running mode on adc 7 (pin A0)
  ADC->ADC_CR = 2;
  ADC->ADC_CHER = 0x80;
  analogWriteResolution(12);
}

int read_adc() {
  while ((ADC->ADC_ISR & 0x80) == 0); // wait for conversion
  int a0 = ADC->ADC_CDR[7];            // read data
  return a0;
}

int calculate_output(int reading) {
  float error = reading - input_setpoint;
  i_term += i_gain * error;
  if (i_term < -4096) {
    i_term = -4096;
  }
  else if (i_term > 4095) {
    i_term = 4095;
  }
  float p_term = p_gain * error;
  return int(p_term + i_term) + input_setpoint;
}

void read_gain() {
  if (Serial.available() > 1) {
     int first_byte = Serial.read();
     if (first_byte == 'P') {
      p_gain = float(Serial.read()-'5');
     }
     else if (first_byte == 'I') {
      i_gain = float(Serial.read()-'5');
      i_gain = i_gain/20;
     }
  }
}

void loop() {
  read_gain();
  int rep = 10;
  int t = micros();
  for (int i = 0; i < rep; i++) {
    int reading = read_adc();
    int output = calculate_output(reading);
    if (output < 0) {
      output = 0;
    }
    else if (output > 4095) {
      output = 4095;
    }
    analogWrite(DAC0, output);
  }
  //Serial.println(i_gain);
  //Serial.println(p_gain);
}

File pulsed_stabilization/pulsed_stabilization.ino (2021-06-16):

int input_setpoint = 2047;
int output_setpoint = 2047;
float p_gain = 1.;
float i_gain = 0.;
float i_term = 0;
//int error_range = 30;
int error[30];
int DIGITALPIN = 8;

void setup() {
  Serial.begin(115200);
  pinMode(DIGITALPIN, INPUT);
  ADC->ADC_MR |= 0x80; // these lines set free running mode on adc 7 (pin A0)
  ADC->ADC_CR = 2;
  ADC->ADC_CHER = 0x80;

  memset(error,0,30);

  analogWriteResolution(12);
  analogWrite(DAC0, output_setpoint);
}

int read_adc() {
  while ((ADC->ADC_ISR & 0x80) == 0); // wait for conversion
  int a0 = ADC->ADC_CDR[7];            // read data
  return a0;
}

//int*array push(array list, int range){
//  for (int i = 0; i <= (range-2); i++){
//    array[i] = array[i+1];
//  }
//  array[range-1] = read_adc()-input_setpoint;
//  return array
//}

void push (int (& list) [30] ){
  for (int i = 0; i < 30-1; i++)
    list[i] = list[i+1]; 
  list[30-1] = read_adc()-input_setpoint;
}

float average (int * array, int range)  // assuming array is int.
{
  long sum = 0L ;  // sum will be larger than an item, long for safety.
  for (int i = 0 ; i < range ; i++)
    sum += array [i] ;
  return  ((float) sum) / range ;  // average will be fractional, so float may be appropriate.
}

void loop() {
  if (digitalRead(DIGITALPIN) == HIGH) {
    while (digitalRead(DIGITALPIN) != LOW) {
      push(error);
    }
    int correction = (int)(average(error, 30));
    output_setpoint += correction;
    analogWrite(DAC0, output_setpoint);
    for (int i = 0; i < 30; i++){
      Serial.println(error[i]);
    }
    Serial.println(output_setpoint);
  }
}

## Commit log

2021-05-23 amp iteration 2
    [non_inverting_amplifier_2.brd, non_inverting_amplifier_2.sch]
2022-07-27 Updated PCB Schematics
    [hole.brd]
2022-07-29 Updated PCBs
    [arduino_board_2iter.brd]
2022-08-04 Updated Arduino PCB for larger size
    [arduino_board_2iter.brd]
2022-08-04 PCB Updates as of 8/4/22
    [arduino_board_2iter.brd, arduino_board_2iter.sch]
2022-08-05 Updated PCB
    [arduino_board_2iter.brd]
2022-08-09 PCB Updates as of 8/9/22
    [arduino_board_2iter.brd, arduino_board_2iter.sch]

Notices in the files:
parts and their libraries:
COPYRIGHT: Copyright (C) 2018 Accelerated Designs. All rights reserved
